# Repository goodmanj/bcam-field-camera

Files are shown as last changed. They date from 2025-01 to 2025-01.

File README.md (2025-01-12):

# BCam - Magnetic Field Camera

## About
BCam lets you see see invisible magnetic fields!  It uses an array of magnetic field sensors to map out the strength and direction of magnetic fields passing through it, displaying the fields on an LCD screen in realtime.  It can sense strong permanent magnets and electromagnets, as well as the weak fields from single current-carrying wires, and the Earth's magnetic field.

BCam is based on the [RP2040 Raspberry Pi Pico](https://www.raspberrypi.com/documentation/microcontrollers/pico-series.html) microcontroller, the [TMAG5273](https://www.ti.com/product/TMAG5273) Hall-effect magnetic field sensor, and the [ILI9488](http://www.lcdwiki.com/3.5inch_SPI_Module_ILI9488_SKU:MSP3520) touch LCD screen.  

BCam was originally designed as a teaching tool for physics classrooms.  The [documentation](doc/) includes demos, lab handouts, and other teaching material.

## Build your own!

This repo contains everything you need to build a BCam:
* [2d/](2d/): 2-d design files (label graphics)
* [pcb/](pcb/): Printed circuit board files
* [src/](src/): Arduino source code
* [cad/](cad/): 3-d design files
* [doc/](doc/): Documentation
* [bom.md](bom.md): Bill of materials

BCam is designed to be built by hand.  All surface-mount parts are hand-solderable (some skill required).  The case is 3-d printed.  You can use a desktop CNC machine to mill your own printed circuit board, or have it made by an online board manufacturer such as [JLCPCB](https://jlcpcb.com/), [PCBWay](https://www.pcbway.com/), or [OSHPark](https://oshpark.com/).

BCam was originally developed as a project for [Fab Academy](https://fabacademy.org/), a hands-on global class in rapid prototyping and digital fabrication.  The original project documentation is [archived at Fab Academy's site](https://fabacademy.org/2023/labs/wheaton/students/jason-goodman/final-project/index.html), but is superseded by this repo.

## Copyright and License

Copyright (c) 2023-2025 Jason Goodman <jcgoodman@gmail.com>

This work is licensed under a
[Creative Commons Attribution-NonCommercial-ShareAlike 4.0 International License][cc-by-nc-sa].

[][cc-by-nc-sa]

[cc-by-nc-sa]: http://creativecommons.org/licenses/by-nc-sa/4.0/
[cc-by-nc-sa-image]: https://licensebuttons.net/l/by-nc-sa/4.0/88x31.png

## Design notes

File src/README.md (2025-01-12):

# src/

This directory contains Arduino source code for BCam.

* [field_camera/](field_camera/): Main program
* [tools/calibrate_field_camera]: Create and store calibration data (field_camera.ino can do this too)
* [tools/fieldcam_test_magnetometers]: Print data from magnetometers to serial port.  Useful for finding soldering problems.

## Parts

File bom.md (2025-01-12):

| Item                                          | Price | Qty   | URL |
|-----------------------------------------------|-------|-------|-------|
| LCD Module Touch Screen ILI9488 480x320 3.5in	| $18.69| 1 	| https://www.amazon.com/gp/product/B09TB78236/|
| TMAG5273A1QDBVR 3D Hall-effect sensor	        | $1.56	| 8	    | https://www.mouser.com/ProductDetail/Texas-Instruments/TMAG5273A1QDBVR|
| TMAG5273B1QDBVR 3D Hall-effect sensor	        | $1.62	| 8	    | https://www.mouser.com/ProductDetail/Texas-Instruments/TMAG5273B1QDBVR|
| TMAG5273C1QDBVR 3D Hall-effect sensor	        | $1.62	| 8	    | https://www.mouser.com/ProductDetail/Texas-Instruments/TMAG5273C1QDBVR|
| Raspberry Pi Pico RP2040 Microcontroller	    | $5.73	| 1	    | https://www.amazon.com/dp/B09437S9X4|
| FR1 Copper Clad - Double Sided 4x6in	        | $1.88	| 1	    | https://www.mouser.com/ProductDetail/SparkFun/TOL-14979|
| Resistor 10.0K 1/4W 1206 SMD	                | $0.10	| 4	    | https://www.mouser.com/ProductDetail/Bourns/CR1206-FX-1002ELF|
| Capacitor 0.1uF 1206 SMD	$                   | 0.26	| 4	    | https://www.mouser.com/ProductDetail/KEMET/C1206C104J1RACAUTO|
| M3 x 20mm stainless steel hex head screws	    | $0.10	| 4	    |               |

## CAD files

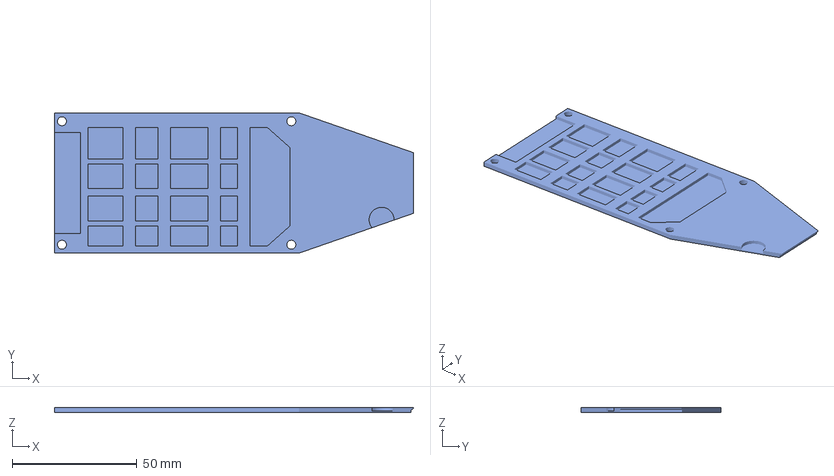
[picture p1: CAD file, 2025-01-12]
cad/field-camera-baseplate.3mf
144.0 x 56.3 x 2.00 mm

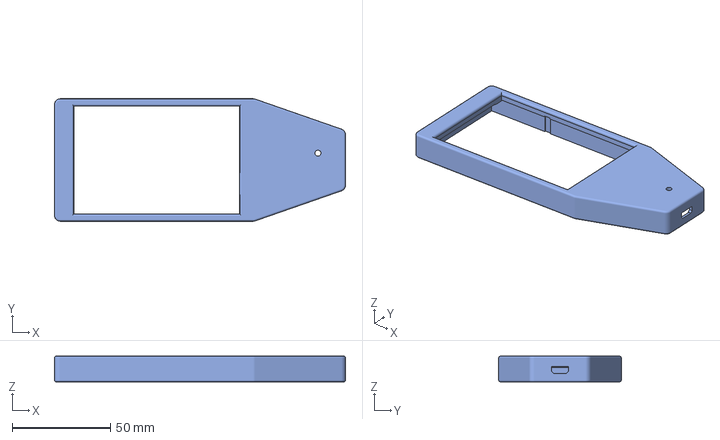
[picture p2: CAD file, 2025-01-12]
cad/field-camera-case.3mf
148.0 x 62.3 x 13.2 mm

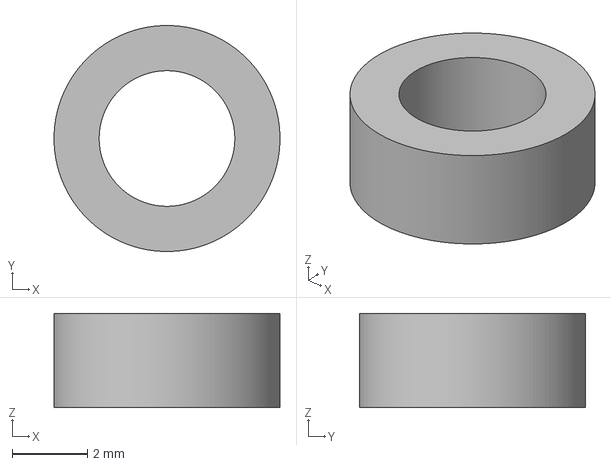
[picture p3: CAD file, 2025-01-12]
cad/field-camera-standoff.3mf
6.00 x 6.00 x 2.50 mm

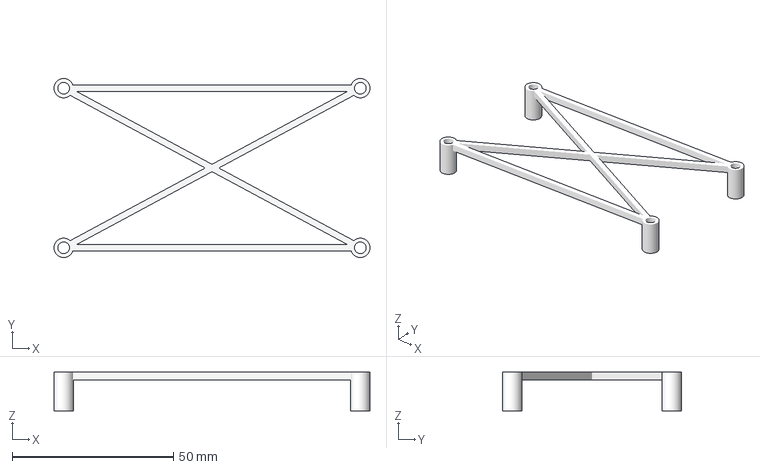
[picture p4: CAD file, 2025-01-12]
cad/field-camera-thick-spacer.3mf
98.0 x 55.5 x 12.0 mm

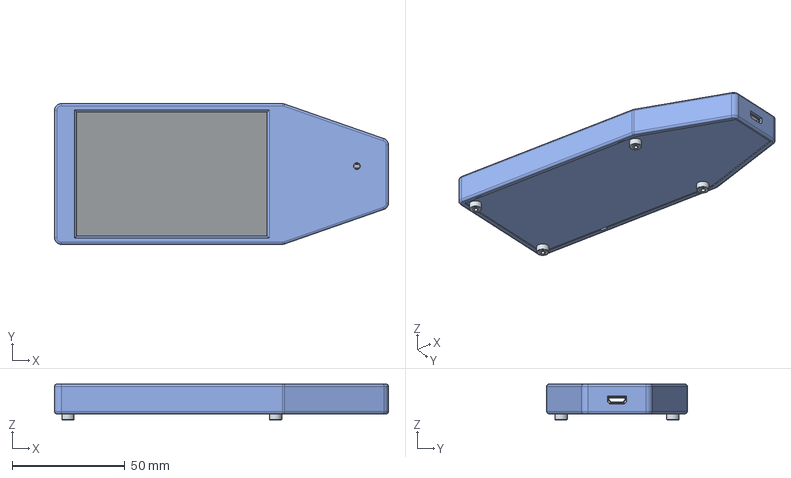
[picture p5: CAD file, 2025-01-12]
cad/field-camera.step
148.0 x 62.3 x 15.9 mm
Case
Hex socket head cap screw M3x0.50 x 10 x 4
Standoff x 2
Baseplate
LCD Panel
LCD Board
LCD Pin Spacer
Sensor
PCB
PICO_REF_USB.STEP x 5
PICO_WINBOND.STEP
PICO_REF_ONSEMI.STEP
PICO_REF_BOARD.STEP
PICO_MURATA.STEP x 2
PICO_REF_MICROCONTROLLER.STEP
PICO_DIODES.STEP
PICO_REF_SWITCH.STEP
PICO_AEL.STEP
PICO_REF_LED.STEP
PICO_RICHTEK.STEP
PICO_BOURNS.STEP

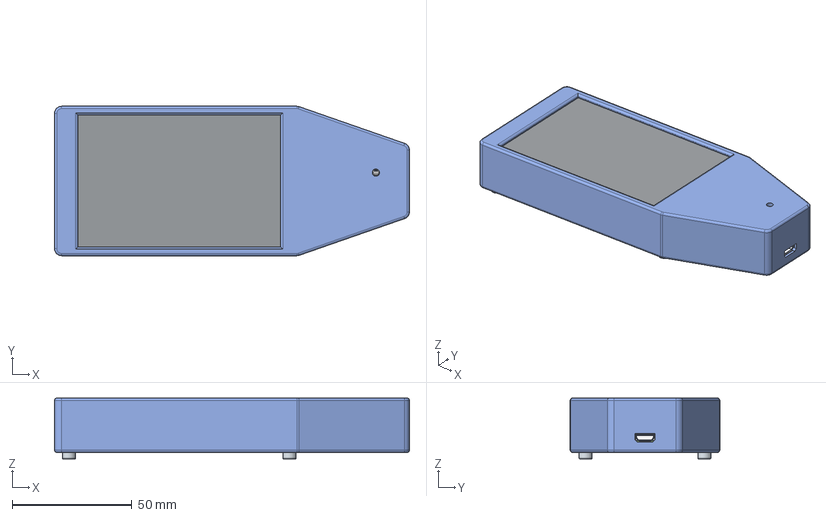
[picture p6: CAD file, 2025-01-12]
cad/field-camera-thick.step
148.0 x 62.3 x 25.4 mm
Case
Hex socket head cap screw M3x0.50 x 10 x 4
Baseplate
LCD Panel
LCD Board
LCD Pin Spacer
Washer
Sensor
PCB
PICO_REF_USB.STEP x 5
PICO_WINBOND.STEP
PICO_REF_ONSEMI.STEP
PICO_REF_BOARD.STEP
PICO_MURATA.STEP x 2
PICO_REF_MICROCONTROLLER.STEP
PICO_DIODES.STEP
PICO_REF_SWITCH.STEP
PICO_AEL.STEP
PICO_REF_LED.STEP
PICO_RICHTEK.STEP
PICO_BOURNS.STEP

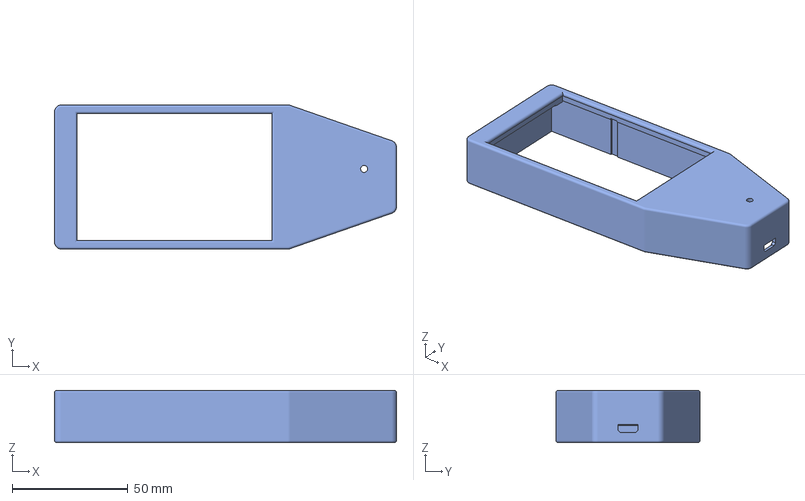
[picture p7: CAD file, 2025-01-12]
cad/field-camera-thick-case.3mf
148.0 x 62.3 x 22.7 mm

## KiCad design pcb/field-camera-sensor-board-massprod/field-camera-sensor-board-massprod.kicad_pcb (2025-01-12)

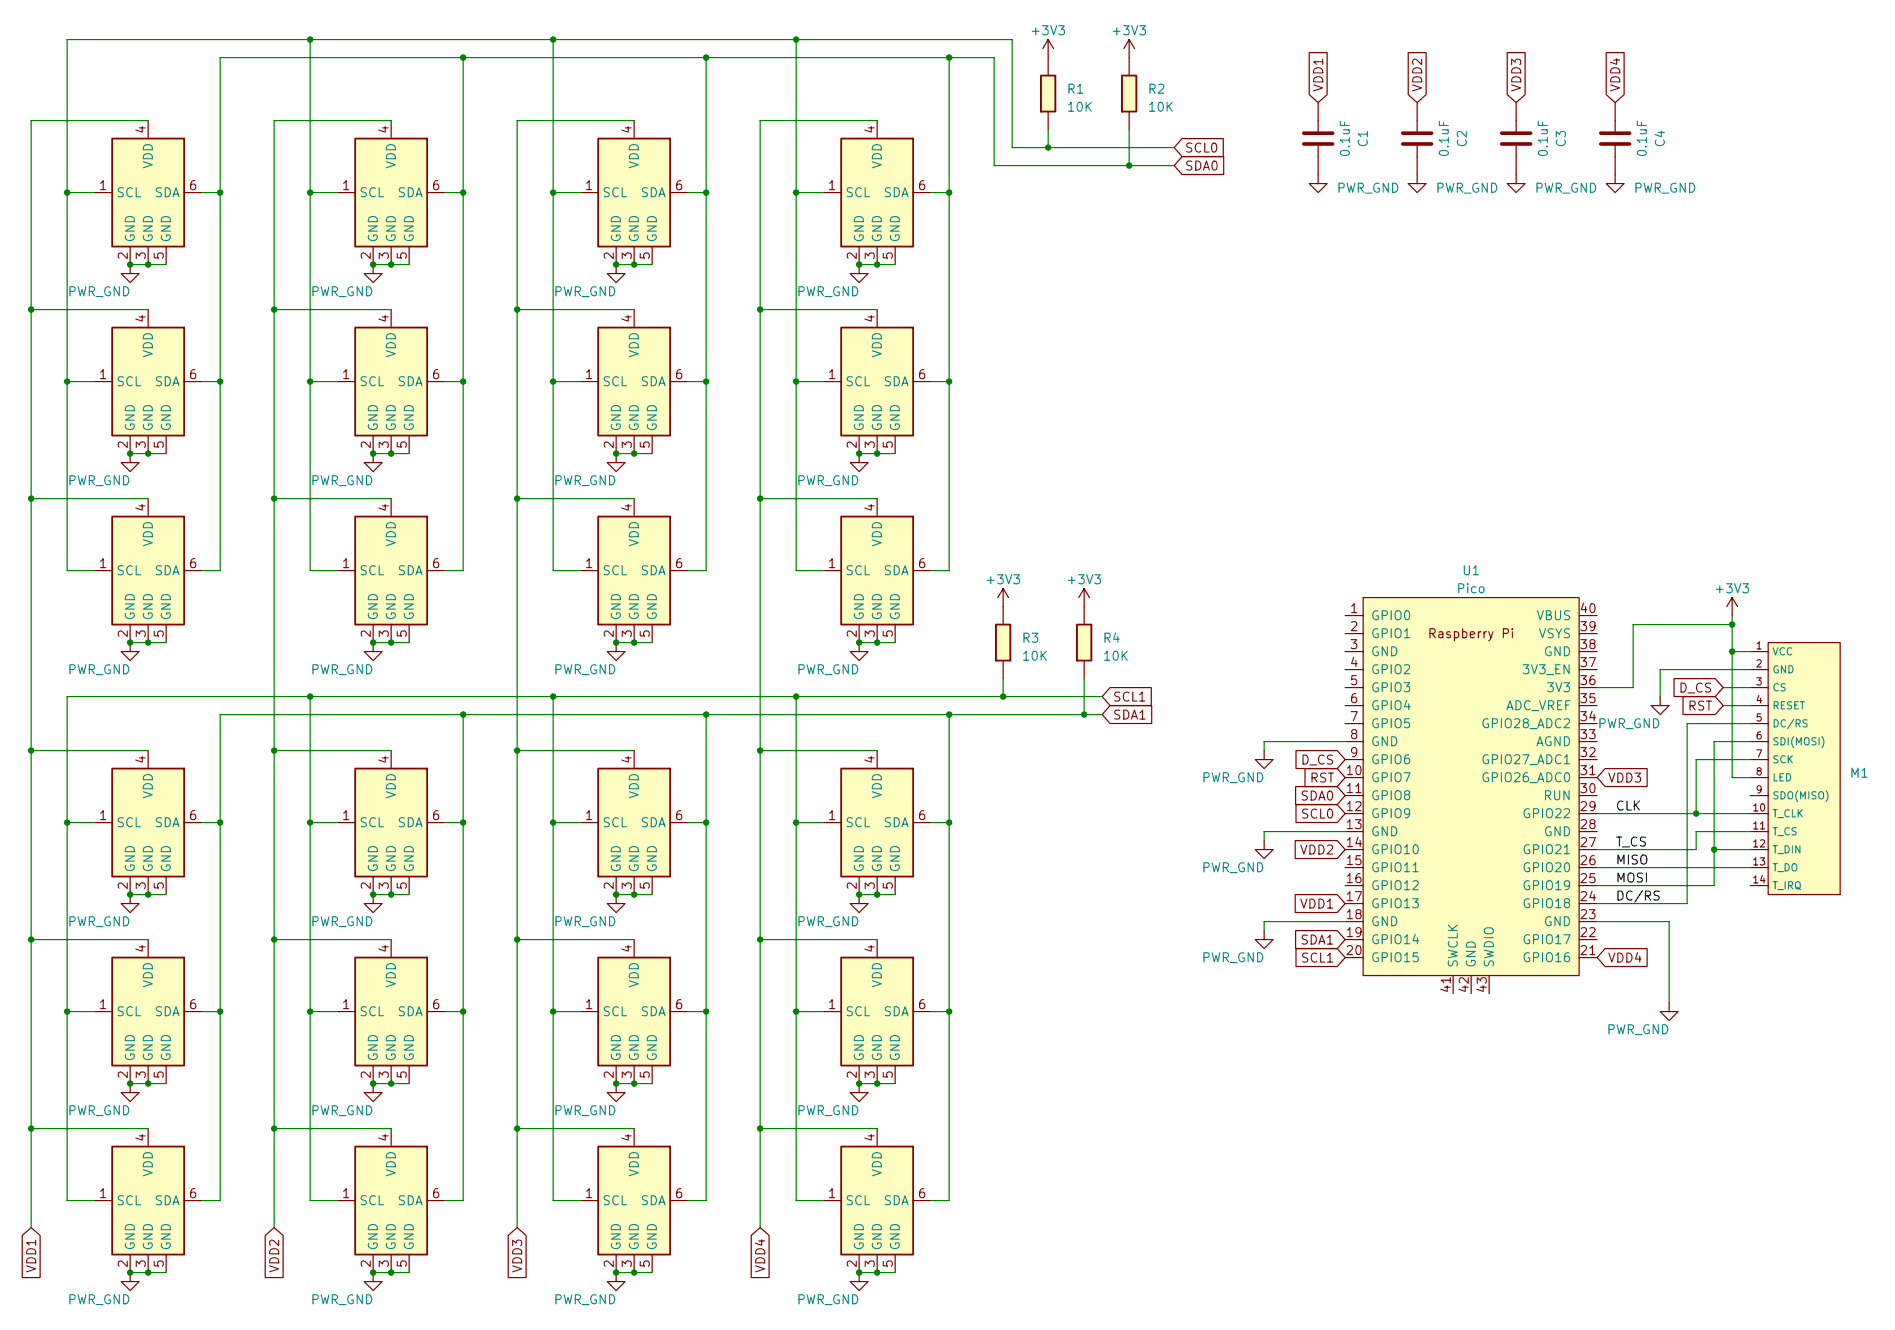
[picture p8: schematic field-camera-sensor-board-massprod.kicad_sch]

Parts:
C1, C2, C3, C4: 0.1uF; C_1206
M1: TFT-3.5-480x320-MSP3520-ILI9488
R1, R2, R3, R4: 10K; R_1206
U0A1, U0A2, U0A3, U0A4, U0B1, U0B2, U0B3, U0B4, U0C1, U0C2, U0C3, U0C4, U1A1, U1A2, U1A3, U1A4, U1B1, U1B2, U1B3, U1B4, U1C1, U1C2, U1C3, U1C4: Sensor_HallEffect_XYZ; TSOT-23-6
U1: Pico; RPi_Pico_SMD_TH

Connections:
+3V3: M1.1 (VCC), M1.8 (LED), R1.1, R2.1, R3.1, R4.1, U1.36 (3V3)
/CLK: M1.7 (SCK), M1.10 (T_CLK), U1.29 (GPIO22)
/DC/RS: M1.5 (DC/RS), U1.24 (GPIO18)
/MISO: M1.13 (T_DO), U1.26 (GPIO20)
/MOSI: M1.6 (SDI(MOSI)), M1.12 (T_DIN), U1.25 (GPIO19)
/T_CS: M1.11 (T_CS), U1.27 (GPIO21)
D_CS: M1.3 (CS), U1.9 (GPIO6)
PWR_GND: C1.2, C2.2, C3.2, C4.2, M1.2 (GND), U0A1.2 (GND), U0A1.3 (GND), U0A1.5 (GND), U0A2.2 (GND), U0A2.3 (GND), U0A2.5 (GND), U0A3.2 (GND), U0A3.3 (GND), U0A3.5 (GND), U0A4.2 (GND), U0A4.3 (GND), U0A4.5 (GND), U0B1.2 (GND), U0B1.3 (GND), U0B1.5 (GND), U0B2.2 (GND), U0B2.3 (GND), U0B2.5 (GND), U0B3.2 (GND), U0B3.3 (GND), U0B3.5 (GND), U0B4.2 (GND), U0B4.3 (GND), U0B4.5 (GND), U0C1.2 (GND), U0C1.3 (GND), U0C1.5 (GND), U0C2.2 (GND), U0C2.3 (GND), U0C2.5 (GND), U0C3.2 (GND), U0C3.3 (GND), U0C3.5 (GND), U0C4.2 (GND), U0C4.3 (GND), U0C4.5 (GND), U1.8 (GND), U1.13 (GND), U1.18 (GND), U1.23 (GND), U1A1.2 (GND), U1A1.3 (GND), U1A1.5 (GND), U1A2.2 (GND), U1A2.3 (GND), U1A2.5 (GND), U1A3.2 (GND), U1A3.3 (GND), U1A3.5 (GND), U1A4.2 (GND), U1A4.3 (GND), U1A4.5 (GND), U1B1.2 (GND), U1B1.3 (GND), U1B1.5 (GND), U1B2.2 (GND), U1B2.3 (GND), U1B2.5 (GND), U1B3.2 (GND), U1B3.3 (GND), U1B3.5 (GND), U1B4.2 (GND), U1B4.3 (GND), U1B4.5 (GND), U1C1.2 (GND), U1C1.3 (GND), U1C1.5 (GND), U1C2.2 (GND), U1C2.3 (GND), U1C2.5 (GND), U1C3.2 (GND), U1C3.3 (GND), U1C3.5 (GND), U1C4.2 (GND), U1C4.3 (GND), U1C4.5 (GND)
RST: M1.4 (RESET), U1.10 (GPIO7)
SCL0: R1.2, U0A1.1 (SCL), U0A2.1 (SCL), U0A3.1 (SCL), U0A4.1 (SCL), U0B1.1 (SCL), U0B2.1 (SCL), U0B3.1 (SCL), U0B4.1 (SCL), U0C1.1 (SCL), U0C2.1 (SCL), U0C3.1 (SCL), U0C4.1 (SCL), U1.12 (GPIO9)
SCL1: R3.2, U1.20 (GPIO15), U1A1.1 (SCL), U1A2.1 (SCL), U1A3.1 (SCL), U1A4.1 (SCL), U1B1.1 (SCL), U1B2.1 (SCL), U1B3.1 (SCL), U1B4.1 (SCL), U1C1.1 (SCL), U1C2.1 (SCL), U1C3.1 (SCL), U1C4.1 (SCL)
SDA0: R2.2, U0A1.6 (SDA), U0A2.6 (SDA), U0A3.6 (SDA), U0A4.6 (SDA), U0B1.6 (SDA), U0B2.6 (SDA), U0B3.6 (SDA), U0B4.6 (SDA), U0C1.6 (SDA), U0C2.6 (SDA), U0C3.6 (SDA), U0C4.6 (SDA), U1.11 (GPIO8)
SDA1: R4.2, U1.19 (GPIO14), U1A1.6 (SDA), U1A2.6 (SDA), U1A3.6 (SDA), U1A4.6 (SDA), U1B1.6 (SDA), U1B2.6 (SDA), U1B3.6 (SDA), U1B4.6 (SDA), U1C1.6 (SDA), U1C2.6 (SDA), U1C3.6 (SDA), U1C4.6 (SDA)
VDD1: C1.1, U0A1.4 (VDD), U0B1.4 (VDD), U0C1.4 (VDD), U1.17 (GPIO13), U1A1.4 (VDD), U1B1.4 (VDD), U1C1.4 (VDD)
VDD2: C2.1, U0A2.4 (VDD), U0B2.4 (VDD), U0C2.4 (VDD), U1.14 (GPIO10), U1A2.4 (VDD), U1B2.4 (VDD), U1C2.4 (VDD)
VDD3: C3.1, U0A3.4 (VDD), U0B3.4 (VDD), U0C3.4 (VDD), U1.31 (GPIO26_ADC0), U1A3.4 (VDD), U1B3.4 (VDD), U1C3.4 (VDD)
VDD4: C4.1, U0A4.4 (VDD), U0B4.4 (VDD), U0C4.4 (VDD), U1.21 (GPIO16), U1A4.4 (VDD), U1B4.4 (VDD), U1C4.4 (VDD)

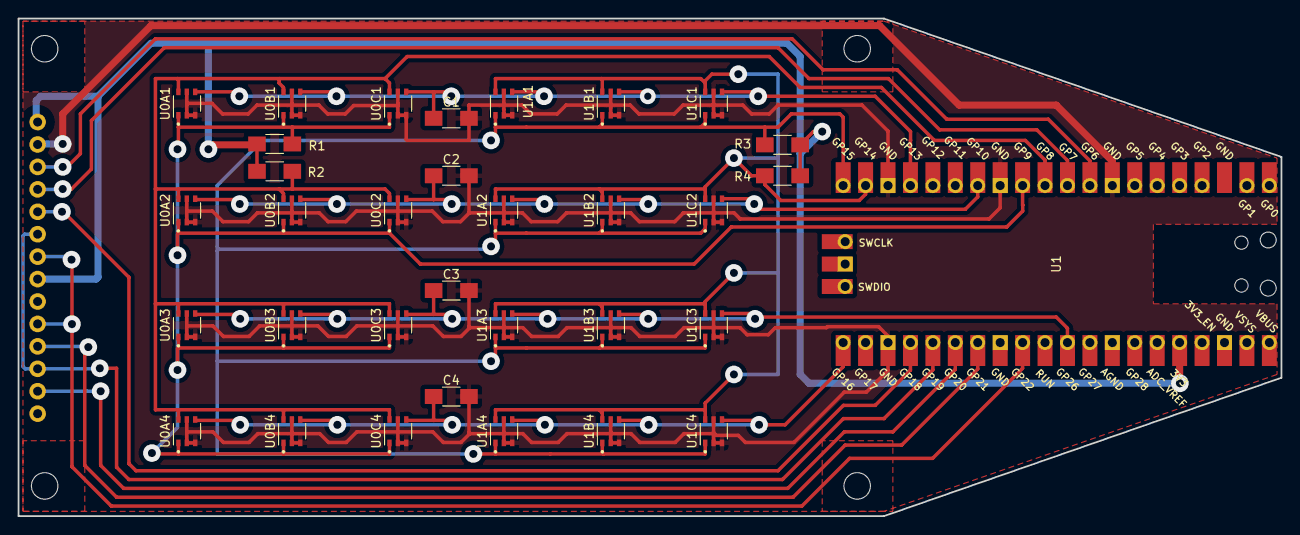
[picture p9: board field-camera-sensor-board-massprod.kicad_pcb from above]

Board: 2 copper layers, 143.0 x 56.3 mm, 34 parts (0 on the bottom side), 17 nets.

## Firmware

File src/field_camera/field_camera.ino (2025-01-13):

/*
    BMAG Magnetic Field Camera

  https://fabacademy.org/2023/labs/wheaton/students/jason-goodman/final-project/index.html

    Copyright (c) 2023-2025 Jason Goodman <jcgoodman@gmail.com>

    Creative Commons License CC BY-NC-SA
    https://creativecommons.org/licenses/by-nc-sa/4.0/

  You are free to:
  Share — copy and redistribute the material in any medium or format
  Adapt — remix, transform, and build upon the material

  Under the following terms:
  Attribution — You must give appropriate credit , provide a link to the license, and indicate if changes were made
  You may do so in any reasonable manner, but not in any way that suggests the licensor endorses you or your use.
  NonCommercial — You may not use the material for commercial purposes .
  ShareAlike — If you remix, transform, or build upon the material, you must distribute your contributions under the same license as the original.
  No additional restrictions — You may not apply legal terms or technological measures that legally restrict others from doing anything the license permits.
*/

// Field Camera: Map and display magnetic fields using an array of 3-d Hall effect magnetometers.

// Magnetometers are laid out in a 2-d array, as follows:
// 0A1 0B1 0C1 1A1 1B1 1C1
// 0A2 0B2 0C2 1A2 1B2 1C2
// 0A3 0B3 0C3 1A3 1B3 1C3
// 0A4 0B4 0C4 1A4 1B4 1C4
//
// where the code indicates:
//    [I2C interface] [Magnetometer model] [Power bus]  

#include <SPI.h>
#include <TFT_eSPI.h>
#include <Wire.h>
#include "TMAG5273.h" 
#include "fieldcam_graphics.h"
#include "LittleFS.h"

// ------------------------------------------------------
// ===== 1. Magnetic field sensor configuration
// ------------------------------------------------------

// Tmag5273 library assumes we're using the TMAG5273A1 with +/- 40 or 80 mT range.  Set this to true
// if you're using the TMAG52783A2 with +/- 133 or 266 mT range.
#define TMAG5273A2_RESCALE false

#define N_I2C_INTS 2 // # of I2C interfaces
#define TMAG1_SDA 14
#define TMAG1_SCL 15
#define TMAG0_SDA 8
#define TMAG0_SCL 9
TMAG5273 tmag5273_i2c0(&Wire);   // Declare one TMAG5273 object for each interface (not each device)
TMAG5273 tmag5273_i2c1(&Wire1);

// Default I2C addresses for TMAG5273 magnetometers, see 
// datasheet https://www.ti.com/lit/ds/symlink/tmag5273.pdf?ts=1686087260323
enum model_id {TMAG_A = 0x35, TMAG_B = 0x22, TMAG_C = 0x78, TMAG_D = 0x44};
#define N_MODELS 3
model_id model_id_list[N_MODELS] = {TMAG_A, TMAG_B, TMAG_C}; // Which models are in our array?


// ------------------------------------------------------
// ===== 2. TFT LCD configuration
// ------------------------------------------------------

#define SCREEN_WIDTH 480
#define SCREEN_HEIGHT 320

TFT_eSPI tft = TFT_eSPI(SCREEN_WIDTH,SCREEN_HEIGHT);  

//uint16_t calData[5] = { 196, 3683, 88, 3707, 1 }; 
uint16_t calData[5] = { 274, 3637, 275, 3449, 1 };// Default touch calibration data

// ------------------------------------------------------
// ===== 3. Magnetometer power configuration
// ------------------------------------------------------

#define N_POWER_PINS 4
int row_power_pin[N_POWER_PINS] = {13,10,26,16};

// ------------------------------------------------------
// ===== 3. Sensor / Screen Interaction configuration
// ------------------------------------------------------

// Total screen width: 73.44 mm, 480 px
// Total screen height: 49 mm, 320 px
// Sensor X positions relative to screen edge (mm): 4.53 16.43 28.43 40.43 52.53 64.18
// Sensor Y positions relative to screen edge (mm): 5.85 17.98 30.99 42.98
// 
#define N_SENSOR_ROWS N_POWER_PINS
#define N_SENSOR_COLUMNS N_I2C_INTS * N_MODELS
const int sensor_x[N_SENSOR_COLUMNS] = {30, 107, 186, 264, 343, 419};
const int sensor_y[N_SENSOR_ROWS] = {38,118,203,281};

// ------------------------------------------------------
// ===== 4. Graphics helper functions and classes
// ------------------------------------------------------

// Defined in fieldcam_graphics.cpp

// ------------------------------------------------------
// ===== 5. UI Settings and Button Handler
// ------------------------------------------------------

// 
// UI Settings
const uint32_t ui_color = TFT_WHITE;  // Pale magenta
const int scale_arrow_pixels = 50; // Size of scale arrow in pixels
const int button_start_x = scale_arrow_pixels + 40;
const int n_scales = 4;
const float scales[] = {0.05,0.5,5,50}; // A vector arrow the size of the scale arrow is this many milliTeslas.
int selected_scale_index = 0; // Which of the field scales is selected?
bool show_xy = true; // Plot XY component of vectors?
bool show_z = true;  // Plot Z component of vectors?

// Button info
const int button_width = 30;
const int button_height = 30;
const int button_top = SCREEN_HEIGHT - button_height;
const int n_buttons = 7;
// Create an array of buttons
Button buttons[n_buttons] = {Button(&tft,"0.05",  button_start_x,button_top,button_width,button_height,TFT_BLACK,ui_color),
                             Button(&tft,"0.5", button_start_x+  button_width,button_top,button_width,button_height,TFT_BLACK,ui_color),
                             Button(&tft,"5",button_start_x+2*button_width,button_top,button_width,button_height,TFT_BLACK,ui_color),
                             Button(&tft,"50",button_start_x+3*button_width,button_top,button_width,button_height,TFT_BLACK,ui_color),
                             Button(&tft,"XY", button_start_x+6*button_width,button_top,button_width,button_height,TFT_BLACK,ui_color),
                             Button(&tft,"Z",  button_start_x+7*button_width,button_top,button_width,button_height,TFT_BLACK,ui_color),
                             Button(&tft,"Cal",  button_start_x+9*button_width,button_top,button_width,button_height,TFT_BLACK,ui_color)};

void handle_buttons(int touch_x, int touch_y) {
  // Screen was touched, did they tap a button?
  for (int i = 0; i< n_buttons; i++) {
    if (buttons[i].touched(touch_x,touch_y)) {
          if (i < n_scales) {// Scale button was pressed
            selected_scale_index = i;
          } else if (buttons[i].text == "XY") { // XY mode button was pressed, toggle
            show_xy = !show_xy;
          } else if (buttons[i].text == "Z")  { // Z mode button was pressed, toggle
            show_z = !show_z;
          } else if (buttons[i].text == "Cal") { // Cal  button was pressed, calibrate
            do_cal();
          }
    }
  }
}

// ------------------------------------------------------
// ===== 7. Sensor array support functions
// ------------------------------------------------------

// Decode x,y location of sensor into an I2C interface, default address, and new address.
void which_sensor(int x, int y, int *i2c_int, int *default_i2c, int *new_i2c) {
  if (x < N_MODELS) {
    *i2c_int = 0;
  } else {
    *i2c_int = 1;
    x = x - N_MODELS;
  }
  *default_i2c = model_id_list[x];
  *new_i2c = *default_i2c + y+1;
}

void setup_tmag(TMAG5273 *device) {
//  device->configOperatingMode(TMAG5273_OPERATING_MODE_STANDBY);
  device->configOperatingMode(TMAG5273_OPERATING_MODE_MEASURE);  // Continuous measurement mode is faster.
  device->configReadMode(TMAG5273_READ_MODE_STANDARD);
  device->configMagRange(TMAG5273_MAG_RANGE_40MT);
  device->configLplnMode(TMAG5273_LOW_NOISE);
  device->configMagTempcoMode(TMAG5273_MAG_TEMPCO_NdBFe);
  device->configConvAvgMode(TMAG5273_CONV_AVG_32X);
  device->configTempChEnabled(true);
  device->initAll();
}

// Scan I2C addresses for debugging purposes
void scanner(TwoWire *wire) {
  byte error, address;
  int nDevices;

  Serial.print("I2C addresses: ");

  nDevices = 0;
  for(address = 1; address < 127; address++ ) 
  {
    // The i2c_scanner uses the return value of
    // the Write.endTransmisstion to see if
    // a device did acknowledge to the address.
    wire->beginTransmission(address);
    error = wire->endTransmission();

    if (error == 0)
    {
      Serial.print("0x");
      if (address<16) 
        Serial.print("0");
      Serial.print(address,HEX);
      Serial.print(" ");

      nDevices++;
    }
    else if (error==4) 
    {
      Serial.print("Unknown error at address 0x");
      if (address<16) 
        Serial.print("0");
      Serial.println(address,HEX);
    }    
  }
  if (nDevices == 0)
    Serial.println("No I2C devices found\n");
  else
    Serial.println("\n");

}

uint8_t read_tmag_sensor(int x,int y,float *Bx_ptr,float *By_ptr,float *Bz_ptr) {
  uint8_t res;
  int i2c_dev,default_i2c_addr, i2c_addr;
  TMAG5273 *tmag_object;
  float T;

  which_sensor(x, y, &i2c_dev, &default_i2c_addr, &i2c_addr);
  if (i2c_dev == 0) {
      tmag_object = &tmag5273_i2c0;
  } else {
      tmag_object = &tmag5273_i2c1;
  }
  tmag_object->switchSensor(i2c_addr); 
  res = tmag_object->readMagneticField(Bx_ptr, By_ptr, Bz_ptr, &T);
  if (TMAG5273A2_RESCALE) {
      *Bx_ptr = *Bx_ptr * 133/40;
      *By_ptr = *By_ptr * 133/40;
      *Bz_ptr = *Bz_ptr * 133/40;
  }
  return res;
}

// ------------------------------------------------------
// ===== 8. Persistent Globals
// ------------------------------------------------------

int dx[N_SENSOR_COLUMNS][N_SENSOR_ROWS], dy[N_SENSOR_COLUMNS][N_SENSOR_ROWS], dz[N_SENSOR_COLUMNS][N_SENSOR_ROWS];
float Bx_smooth[N_SENSOR_COLUMNS][N_SENSOR_ROWS], By_smooth[N_SENSOR_COLUMNS][N_SENSOR_ROWS], Bz_smooth[N_SENSOR_COLUMNS][N_SENSOR_ROWS];
bool available[N_SENSOR_COLUMNS][N_SENSOR_ROWS];  // True if sensor is available

/* Calibration data */
float Bx_cal_zero[N_SENSOR_COLUMNS][N_SENSOR_ROWS];
float By_cal_zero[N_SENSOR_COLUMNS][N_SENSOR_ROWS];
float Bz_cal_zero[N_SENSOR_COLUMNS][N_SENSOR_ROWS];

// ------------------------------------------------------
// ===== 9. Calibration  Helper Functions
// ------------------------------------------------------

void print_cal_data(Stream *s, float field[N_SENSOR_COLUMNS][N_SENSOR_ROWS]) {
  for (int x=0; x<N_SENSOR_COLUMNS; x++) {// Print out C++ array definition format
    for (int y=0; y < N_SENSOR_ROWS; y++) {
      s->print(field[x][y],4);
      if (y==N_SENSOR_ROWS-1) {
        s->println("");
      } else {
        s->print(", ");                  
      }
    }
  }
 }

void read_cal_data(Stream *s, float field[N_SENSOR_COLUMNS][N_SENSOR_ROWS]) {
  int x,y;
  for (int x=0; x<N_SENSOR_COLUMNS; x++) {// Print out C++ array definition format
    for (int y=0; y < N_SENSOR_ROWS; y++) {
      if (s->available()) {
        field[x][y] = s->parseFloat();
      } else {
        field[x][y] = 0.;
      }
    }
  }
}

void read_calib_file() {
  File f = LittleFS.open("tmag_cal.csv","r");
  read_cal_data(&f, Bx_cal_zero);
  read_cal_data(&f, By_cal_zero);
  read_cal_data(&f, Bz_cal_zero);
  Serial.println("Bx_cal_zero = ");
  print_cal_data(&Serial,Bx_cal_zero);
  Serial.println("By_cal_zero = ");
  print_cal_data(&Serial,By_cal_zero);
  Serial.println("Bz_cal_zero = ");
  print_cal_data(&Serial,By_cal_zero);
}
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

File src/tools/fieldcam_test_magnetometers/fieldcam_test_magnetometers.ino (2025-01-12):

#include <Arduino.h>
#include <Wire.h>

#include "TMAG5273.h"

#define N_I2C_INTS 2
#define TMAG1_SDA 14
#define TMAG1_SCL 15
#define TMAG0_SDA 8
#define TMAG0_SCL 9
TMAG5273 tmag5273_i2c0(&Wire);
TMAG5273 tmag5273_i2c1(&Wire1);

enum model_id {TMAG_A = 0x35, TMAG_B = 0x22, TMAG_C = 0x78, TMAG_D = 0x44};
//#define N_MODELS 3
//model_id model_id_list[N_MODELS] = {TMAG_A,TMAG_B,TMAG_C};
#define N_MODELS 3
model_id model_id_list[N_MODELS] = {TMAG_A, TMAG_B, TMAG_C};

#define N_POWER_PINS 4
int row_power_pin[N_POWER_PINS] = {13,10,26,16};
//int row_power_pin[N_POWER_PINS] = {10};
//int row_power_pin[N_POWER_PINS] = {13,26,16};

#define N_Y N_POWER_PINS
#define N_X N_I2C_INTS * N_MODELS

bool available[N_X][N_Y];  // True if sensor is available

// Decode x,y location of sensor into an I2C interface, default address, and new address.
void which_sensor(int x, int y, int *i2c_int, int *default_i2c, int *new_i2c) {
  if (x < N_MODELS) {
    *i2c_int = 0;
  } else {
    *i2c_int = 1;
    x = x - N_MODELS;
  }
  *default_i2c = model_id_list[x];
  *new_i2c = *default_i2c + y+1;
}

void setup_tmag(TMAG5273 *device) {
  device->configOperatingMode(TMAG5273_OPERATING_MODE_STANDBY);
  device->configReadMode(TMAG5273_READ_MODE_STANDARD);
  device->configMagRange(TMAG5273_MAG_RANGE_40MT);
  device->configLplnMode(TMAG5273_LOW_NOISE);
  device->configMagTempcoMode(TMAG5273_MAG_TEMPCO_NdBFe);
  device->configConvAvgMode(TMAG5273_CONV_AVG_32X);
  device->configTempChEnabled(true);
  device->initAll();
}

void setup() 
{
  int x,y;
  model_id model;
  int i2c_dev, default_i2c_addr, new_i2c_addr;
  TMAG5273 *tmag_object;
  byte error;

  Serial.begin(115200);
  while (!Serial); 
  Serial.println("Starting I2C0");
  Wire.setSDA(TMAG0_SDA);
  Wire.setSCL(TMAG0_SCL);
  Wire.begin();
  Wire.setClock(1000000);

  Serial.println("Starting I2C1");
  Wire1.setSDA(TMAG1_SDA);
  Wire1.setSCL(TMAG1_SCL);
  Wire1.begin();
  Wire1.setClock(1000000);
  
  for (y=0; y < N_Y; y++) {
    Serial.print("Activating power bus ");
    Serial.println(row_power_pin[y]);
    pinMode(row_power_pin[y],OUTPUT);
    digitalWrite(row_power_pin[y],HIGH);
    delay(1);
    Serial.println("Scanning I2C0");
    scanner(&Wire);
    Serial.println("Scanning I2C1");
    scanner(&Wire1);
    delay(1);
    for (x=0; x<N_X; x++) {
      which_sensor(x, y, &i2c_dev, &default_i2c_addr, &new_i2c_addr);

      Serial.print("Configuring sensor x=");
      Serial.print(x);
      Serial.print(", y=");
      Serial.print(y);
      Serial.print(" from I2C");
      Serial.print(i2c_dev);
      Serial.print(" 0x");
      Serial.print(default_i2c_addr,HEX);
      Serial.print(" to  0x");
      Serial.println(new_i2c_addr,HEX);
      if (i2c_dev == 0) {
        tmag_object = &tmag5273_i2c0;
      } else {
        tmag_object = &tmag5273_i2c1;
      }
      tmag_object->switchSensor(default_i2c_addr);
      tmag_object->modifyI2CAddress(new_i2c_addr); // change I2C address
      delay(1);
      if (i2c_dev == 0) {
        Wire.beginTransmission(new_i2c_addr);
        error = Wire.endTransmission();
      } else {
        Wire1.beginTransmission(new_i2c_addr);
        error = Wire1.endTransmission();
      }
      available[x][y] = (error == 0);
    }
    Serial.println("Scanning I2C0");
    scanner(&Wire);
    Serial.println("Scanning I2C1");
    scanner(&Wire1);
  }
  Serial.println("Sensor availability:");
  for (y=0; y < N_Y; y++) {
      for (x=0; x<N_X; x++) {
        Serial.print(available[x][y]?"+":"-");
      }
    Serial.println("");
  }
  setup_tmag(&tmag5273_i2c0);
  setup_tmag(&tmag5273_i2c1);
}
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

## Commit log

2025-01-12 First copy from Fab Academy repo
    [field-camera-baseplate.3mf, field-camera-case.3mf, field-camera-sensor-board-massprod.kicad_pcb, field-camera-sensor-board-massprod.kicad_sch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]
2025-01-13 Test for sensor availability
